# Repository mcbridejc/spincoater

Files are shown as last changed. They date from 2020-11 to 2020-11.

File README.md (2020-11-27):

# Spin Coater

A spin coater is a piece of lab equipment used to apply a liquid as a thin 
film onto a flat surface. When I looked at spin coaters to buy, most were 
surprisingly expensive (>$1000), and the cheaper ones that I found were too
small for me. It isn't really a very complicated device, and it's fun to build things, so 
I ended up building my own.

Here I've tried to document the project, in case anyone else thinking about 
building something similar comes along and may find it helpful. 
Feel free to reproduce, or to use for inspiration in designing your 
own version.

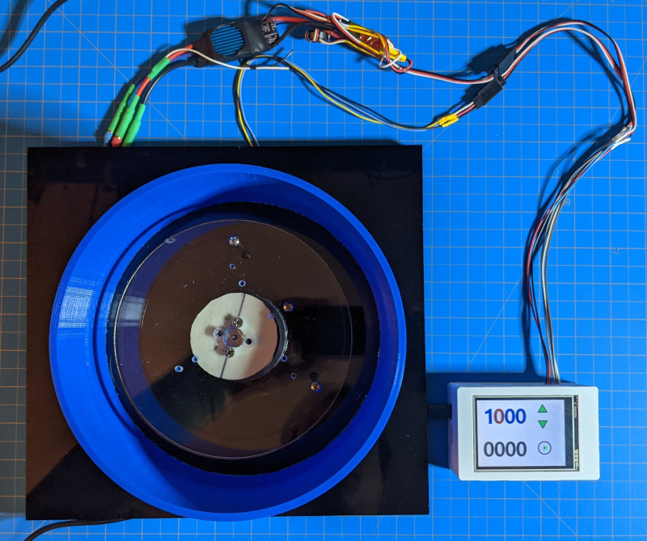
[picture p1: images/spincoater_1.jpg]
Spincoater


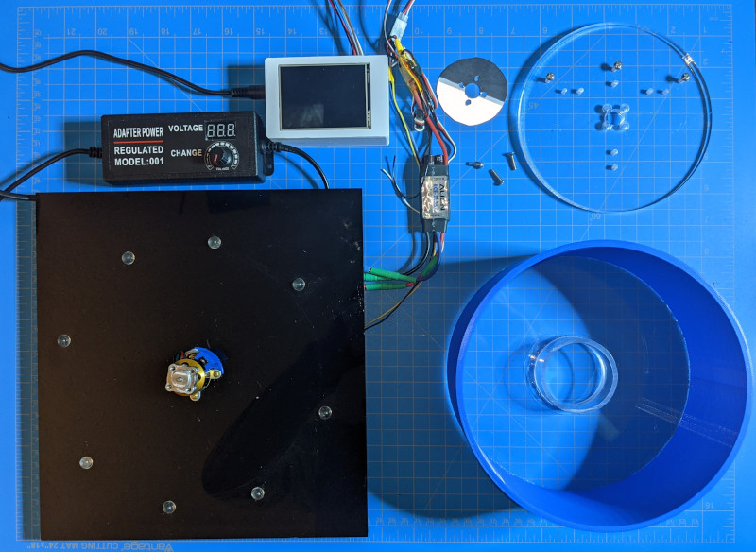
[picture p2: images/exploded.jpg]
Exploded view of spin coater parts


# The Design

The needed elements are simple: 
- A motor which can maintain a controlled RPM
- A way to mount the thing-to-be-coated to the motor
- An enclosure to catch the excess fluid and catch any shrapnel if things go badly

## The Motor

The motor is a A2212 1000KV hobby quadcopter motor, like [this one](https://www.amazon.com/gp/product/B075ZSDR2T/)
. I bought this along with an ESC for $16 on amazon. These are good because they 
are readily available and cheap, but they're not reallly ideal for a spin 
coater. They are designed for fairly high speeds, and because they are 
sensorless -- using the back-EMF voltage to commutate the motor -- they have to do
an open loop startup to get up to speed and they don't work below a certain RPM.
I've found that with this controller/motor combo I can't run slower than 500RPM.

A sensored motor would be better, but I didn't find any cheap options 
for these. There are some sensored RC car motors out there apparently, but by the 
time I saw those I had this working and they aren't *that* cheap. With this setup,
there isn't any feedback on RPM from the ESC. The ESC certainly knows the speed, 
but I have no way to access it, so I had to add speed sensing anyway.

One day, maybe, I'd like to replace the ESC with a custom
motor controller using an STSPIN dev board. Since the load on the motor in this
case is pretty predictable, and I'm not very worried about power efficiency,
I think a fully open loop commutation would work fine, and would eliminate
the need for a speed sensor. At the moment though the current setup is meeting
my needs so I don't feel much pressure to put any more time into it.

## The Chuck

A good spin coater usually has a vacuum chuck, so that the item being spun can
be placed on and off easily by switching the vacuum. This is convenient, but 
it requires getting vaccum through a spinning shaft, and it requires a vacuum
pump. I opted for a simpler attachment mechanism using screws. I laser cut a 
piece of acrylic to serve as the chuck, with tapped 6-32 holes for screws. I could
put these at the right spot because I knew the size of the things I wanted to 
spin coat. It's possible to tape the substrate onto the disk as well for more
flexible mounting. Both of these prevent the coating from covering all the way
out to the edges of the substrate. This was fine for me, but if you need 100%
coverage...well the vacuum chuck starts to look pretty useful now, doesn't it?

The base (left), and chuck (right), are laser cut from 1/4 and 3/8 inch thick acrylic sheets:

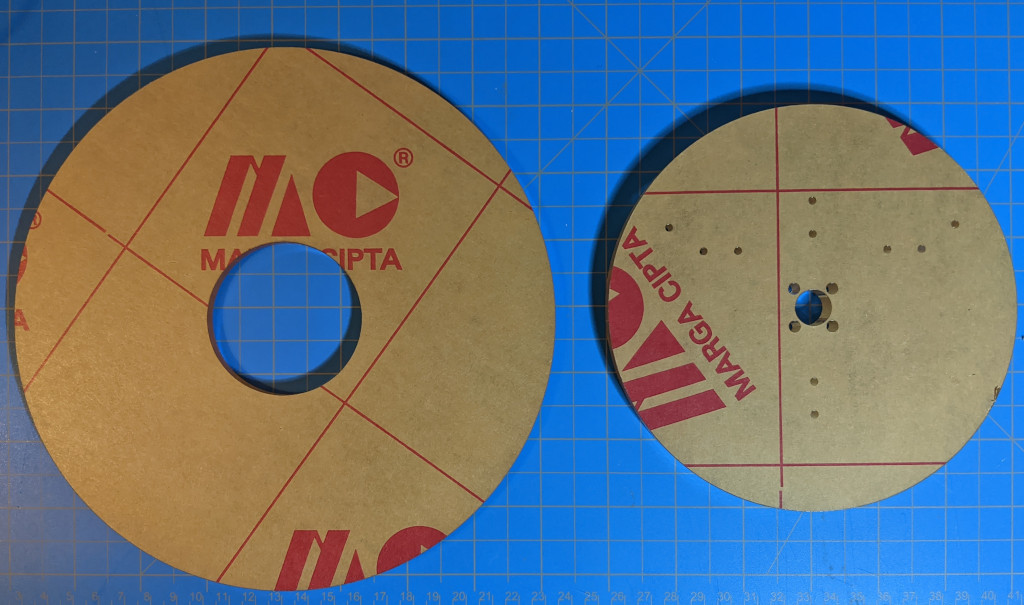
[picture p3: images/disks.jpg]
Laser cut base and chuck disks


It mounts to the motor shaft using a [set screw hub from servocity](https://www.servocity.com/0-125-0-770-set-screw-hub/).

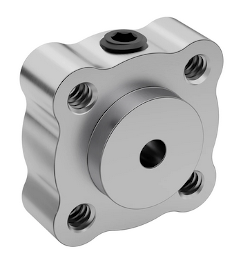
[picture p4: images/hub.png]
Hub


For the tapped holes, I laser cut under-sized holes to mark location, and drilled them afterwards for precise hole size before tapping. 

## The Enclosure

A spin coater needs an enclosure. This is a safety concern, for sure -- nobody 
wants objects coming loose and flying off with high energy, especially not 
glass objects. But also, even when nothing goes wrong, most of the 
applied liquid is going to get flung in all directions so you need
something to contain the mess.  

Someone suggested to me that I could just put the motor in a bucket, and this 
struck me as a very sensible idea. I expect this sort of sensibility makes this
person much more productive than I am. Still though, I eschewed the bucket because
a) I wanted something prettier, b) I wanted it the size I wanted it, and c)
it's partly about the journey for this project. 

Here's a second -- probably better -- way to build an enclosure that I chose 
not to do: laser cut a square box in the classic finger joint manner. The only downside
I see is that it wil be harder to clean gunk out of the corners -- if you're
the type of person that might clean their spin coater, that is. 

Here's the most interesting thing I tried, but also probably terrible: 

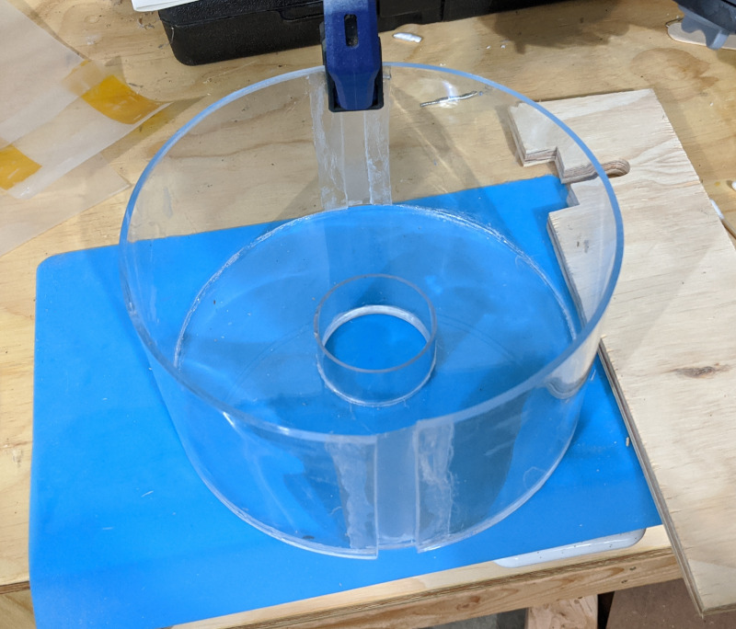
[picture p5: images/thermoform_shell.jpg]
Thermformed enclosure


It's interesting because I had never thermoformed acrylic before, but I watched 
a youtube video and I wanted to try it for myself. I'm glad I did it, but it was
kind of a lot of work and the final result wasn't great. Functional -- I actually 
used this enclosure for a few months -- but still I don't really recommend this method. 
With some practice and a better mold -- more work! -- it could probably get better,
but I moved on.

The bottom plate is laser-cut acylric sheet. The inner wall is a polycarbonate tube
from McMaster, and the gaps between the two molded acrylic walls is covered with 
a thin polycarbonate film. All of this is glued together with Scigrip 16 acrylic cement.

I built a very simple form out of two laser cut acrylic disks fitted onto the extra polycarb 
tube used for the inner wall. I cut an acrylic sheet to size by scoring and breaking it. 
This I placed into my oven to heat, and it comes out as a satisfyingly jiggly but solid
sheet of plastic, which can be laid over the form to cool in the right shape. 

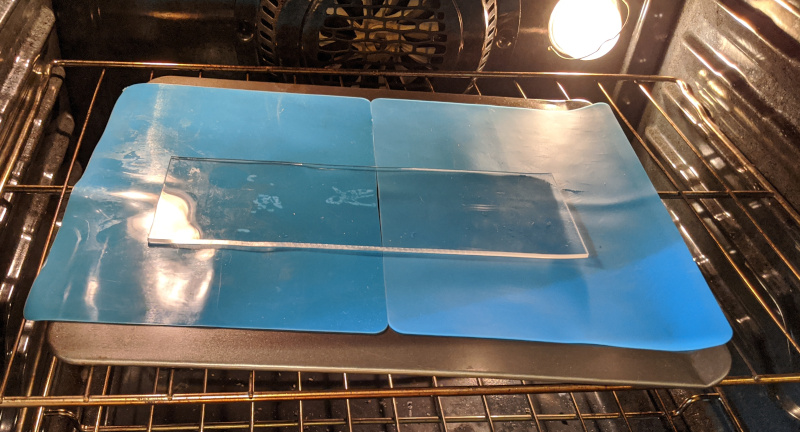
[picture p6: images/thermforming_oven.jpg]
Plastic sheet heating in oven


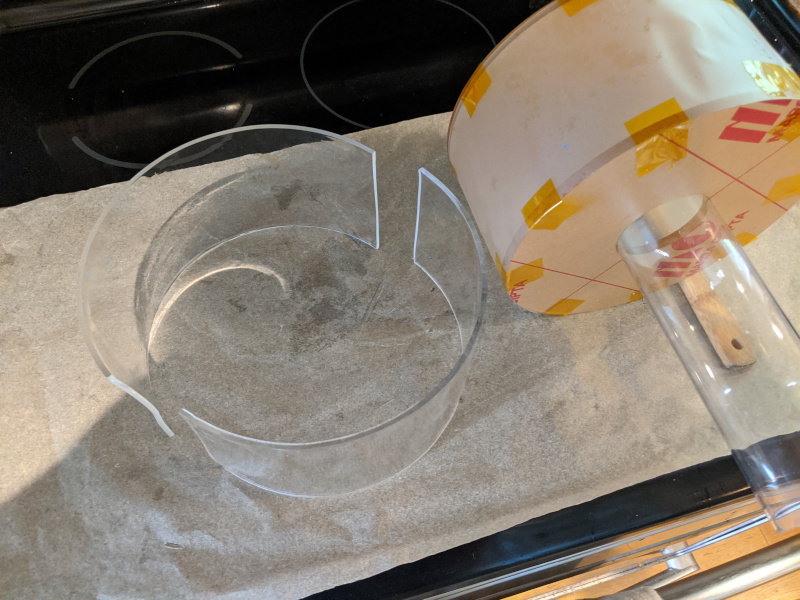
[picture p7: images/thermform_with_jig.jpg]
Formed pieces and forming jig


While using the thermoformed enclosure, I acquired a 3D printer -- Covid has really increased
the value of having tools at home -- and the enclosure size I wanted 
*just* fit into the work area of the printer. It was
a 15 hour job, but hardly took any of my time. Also, it looks much better. Here's
the final product:

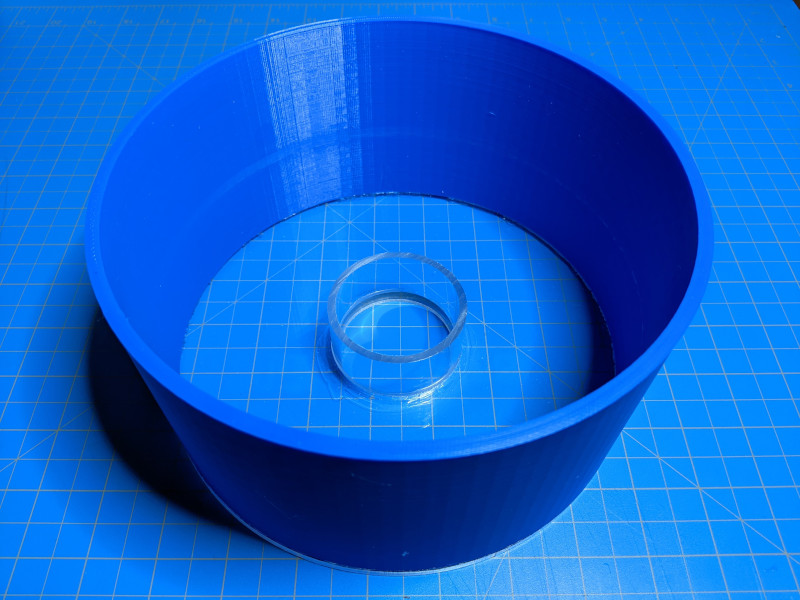
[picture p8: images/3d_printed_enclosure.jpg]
3D Printed Enclosure


The whole thing *could* be 3D printed, but I already had the laser cut bottom and that
saves a lot of print time. The only part I would not want to 3D print is the chuck, 
just because of the tapped holes for the mounting screws.

The motor is mounted to a larger square acrylic base plate, and the round enclosure sits
on top of that, held in place by stick-on rubber bumbers. The bottom plate has
some tall feet to leave a bit of clearance for wires to run out underneath. This 
bottom sheet isn't really necessary; to be honest I ended up this way just 
because I already had the motor mounted to this sheet of acrylic from another 
project.

## Speed Measurement

### Phase Voltage: Tried and abandoned

The first method I used to measure RPM was tapping the voltage off of one of
the motor phases, and filtering to generate a digital signal. This actually 
worked, and I used it for a while, but it was finicky.
It had to be tuned just right, and it only worked 
reliably for a narrow motor input voltage range. Secondly, it was dependent on the 
particular ESC waveform; when I tried it with a different ESC it didn't work 
at all, and at that point I threw it out and dug into my parts drawers for an optical sensor.

### Optical Encoder: Time tested, tinkerer approved

For take two of the speed sensor, I setup a QRD1114 reflective sensor next to the motor, and mounted a half-dark, half-bright disk underneath the chuck. A 3D printed mount holds the 
sensor in place. The sensor is hot-glued into the mounting bracket, and the 
bracket is attached to the baseplate with 3M LSE300 pressure sensitive adhesive. 
The black and white disk is just cut from a sheet of thin (0.2mm) G10 I had around, with some paper glued on, but could be made of anything with enough rigidity
to hold itself up. Or you could just glue a piece of paper to the chuck.

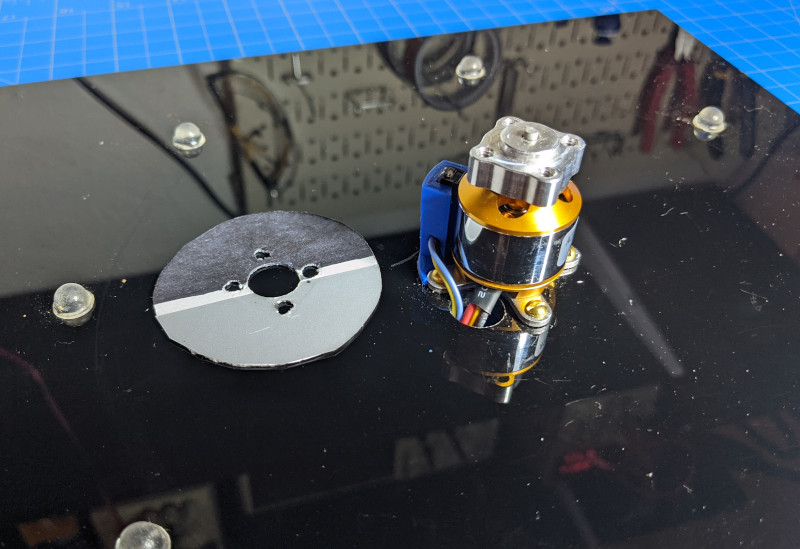
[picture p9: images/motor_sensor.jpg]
Motor and sensor mounted on base


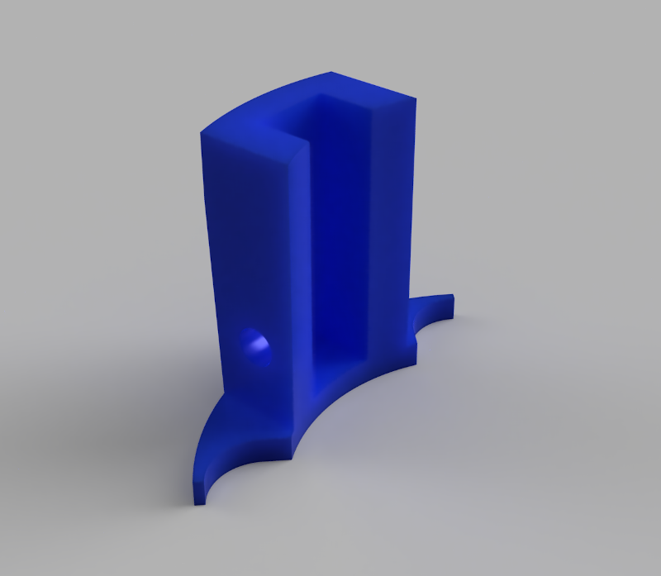
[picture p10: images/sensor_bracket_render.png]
Render of sensor bracket


This repo includes the 3D models for the bracket as [STEP](3dmodels/SensorBracket.step) or [STL](3dmodels/SensorBracket.stl)

Controller
----------

The controller is based on an STM32 microcontroller with a touchscreen. All it needs to do is 
measure the spindle speed and adjust the PWM output to the ESC to regulate 
to the desired speed.

It uses the [Tapper](https://github.com/mcbridejc/tapper) board, with just
a few resistors and a trim pot added to adjust the photodiode sensitivity 
on the speed sensor.

The software for the controller can be found at https://github.com/mcbridejc/spincoater-controller.

## Parts List

| Name           | Supplier     | Part Number | Description |
| ---------------| ------------ | ----------- | ----------- |
| Base               | Tap Plastics | N/A         | 10x10x0.25" acrylic from the scrap bin |
| Inner Wall         | McMaster     | 8585K29     | Polycarb tube 2-1/4" OD, 1/8" thick |
| Rubber Bumpers     | McMaster     | 95495K57    | Clear bumpers with adhesive |
| Motor Hub          | Servocity    | 545540      | 0.77" Set Screw Hub with 1/8" bore ([link](https://www.servocity.com/0-125-0-770-set-screw-hub/)) |
| Reflectance sensor | Digikey      | QRD1114     | LED and Phototransistor in leaded package |
| Motor              | Amazon       | A2212/13T   | 1000kV, 14 pole pair brushless motor |
| Thermoformed walls |  | N/A | 1/8" acrylic sheet, cut to size, and molded |
| Enclosure bottom   |  | N/A | 1/8" acrylic sheet, laser cut |
| Chuck Disk         |  | N/A | 3/8" acrylic sheet, laser cut |

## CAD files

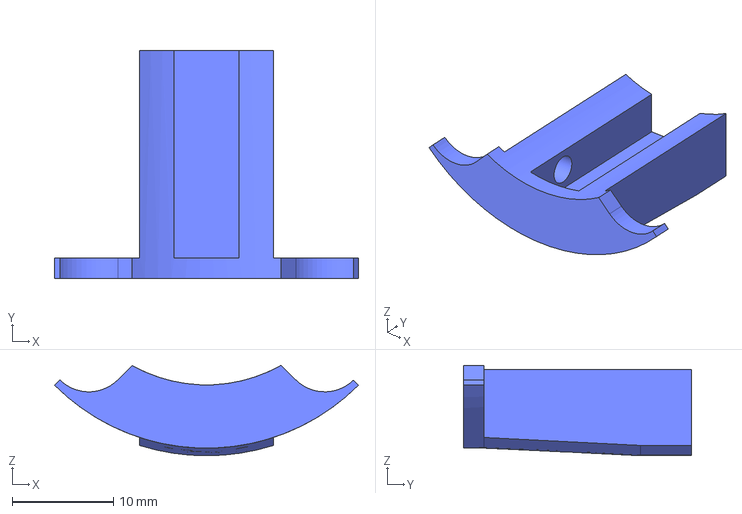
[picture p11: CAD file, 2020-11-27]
3dmodels/SensorBracket.step
30.1 x 22.5 x 8.94 mm

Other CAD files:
3dmodels/SensorBracket.stl
